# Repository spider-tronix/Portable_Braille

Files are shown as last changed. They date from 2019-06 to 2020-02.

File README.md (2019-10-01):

# Portable Braille

## Abstract:
Braille is a system of raised dots that allows visually impaired people to read tactilely. Currently, the number of books written in Braille script is less and the cost is high. This project is an approach to solve the problem of unavailability of many of the books and texts in Braille script. The Portable Braille consists of a camera module which captures the image of a printed text material and converts it into text format by using Optical Character Recognition(OCR). The characters in the text are converted into Braille characters(3x2 matrix form) and fed to the actuators. The actuators are the pins in the head of a dot matrix printer. The pins are actuated in such a way that it creates pressure at required points in the fingertip similar to how pressure felt when placed on an embossed braille character. By this way the device sends character by character to the user’s fingertip through the actuators.
These characters will be sent with appropriate delays to make the user understand words/sentences. Hence a given printed text material can be understood by the blind person through his/her sense of touch.

## Team:

  • [Aditya Kumar Singh](https://github.com/adityasingh3007)

  • [Raj Kumar Bhagat](https://github.com/Rajk0520)

  • [Ruphan S](https://github.com/ruphan)

  • [Yash Patel](https://github.com/yash270200)

## Working Video Demonstration:

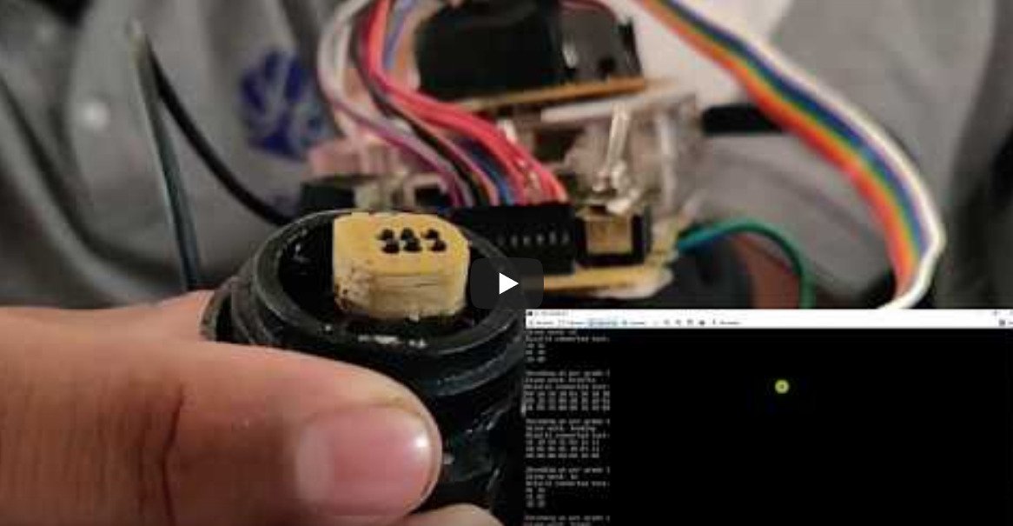
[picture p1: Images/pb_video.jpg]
(https://youtu.be/wZ1dMdXMtPE)

    
# Repository Organized.

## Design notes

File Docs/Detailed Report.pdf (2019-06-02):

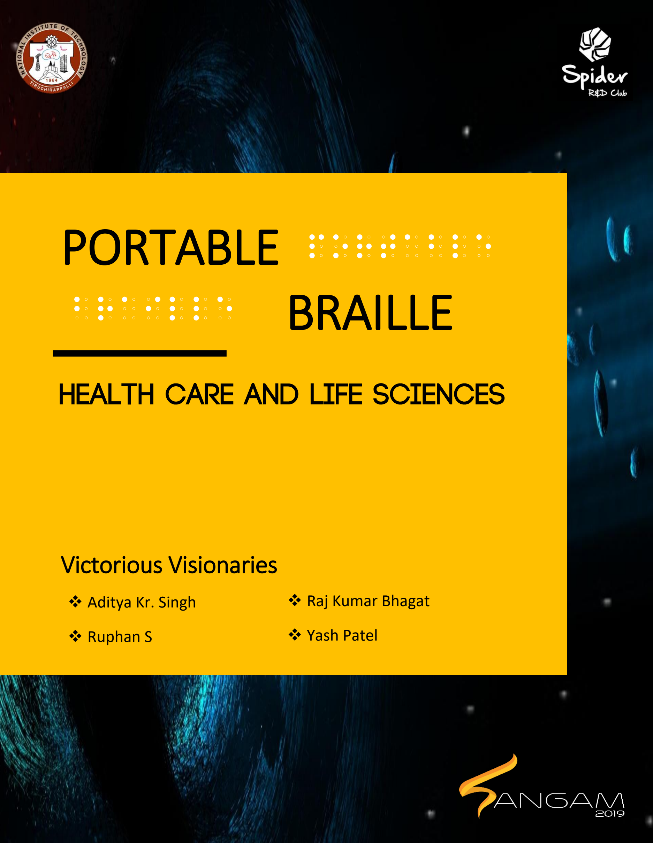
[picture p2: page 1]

1

# PORTABLE BRAILLE

## ❖ Aditya Kr. Singh

## ❖ Ruphan S

# Victorious Visionaries

# portable

# braille

## ❖ Raj Kumar Bhagat

## ❖ Yash Patel

## Portable Braille

2

# Table of Contents

### Project – Portable Braille System | 1

### Table of Contents | 2

1. | Introduction | | 3
2. | Proposed Solution (in Nutshell) | | 4
3. | Technical Details | | 5
3.1 Image Capturing | 5
3.2 OCR | 5
3.3 Braille Conversion | 6
3.4 Actuation | 7
4. | Extension | | 8
5. | Innovativeness | | 8
6. | Components and Cost | | 9
7. | Timeline | | 10
8. | Statistics and Impacts | | 11

3

B
raille is a system of raised dots that allows visually impaired people to read tactilely. Braille symbols are formed within units of space known as braille cells. A full braille cell consists of six raised dots arranged in two parallel rows each having three dots. The dot positions are identified by numbers from one through six. A single cell can be used to represent an alphabet letter, number, punctuation mark, or even a whole word depending upon the grade used. Braille is not just a language, rather it’s a code by means of which other languages such as English, Spanish, Arabic, and dozens of others may be read. Also, Braille defines the blind literacy. A blind person is considered to be a literate only if he/she knows to read Braille, hence making Braille a day-to-day need for the blind. This is also one of the main reason why Braille is still a standard and not completely obsolete.

Currently, the number of books written in Braille script are less and the cost is high. This project is an approach to solve the problem of unavailability of many of the books and texts in Braille script. The Portable Braille consists of a camera module which captures the image of a printed text material and converts it into text format by using Optical Character Recognition(OCR). The characters in the text are converted into Braille characters(3x2 matrix form) and fed to the actuators. The actuators are the pins in the head of a dot matrix printer. The pins are actuated in such a way that it creates pressure at required points in the fingertip similar to how pressure is felt when placed on an embossed braille character. The device sends character by character to the user’s fingertip through the actuators. These characters will be sent with appropriate delays to make the user understand words/sentences. Hence a given printed text material can be understood by the blind person through his/her sense of touch.

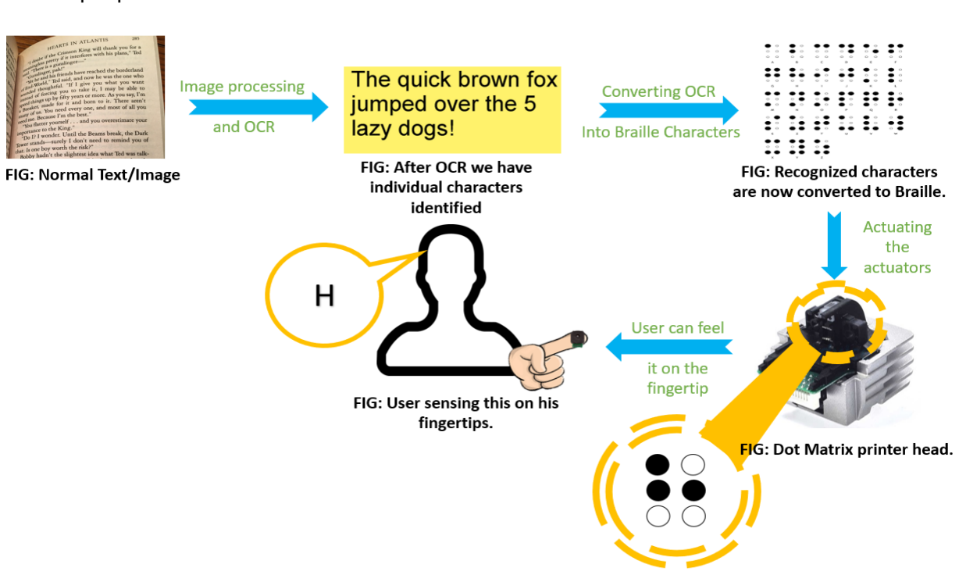
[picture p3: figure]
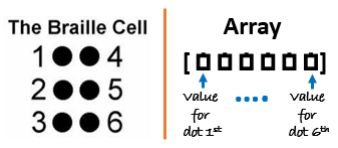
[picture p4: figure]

4

# (in Nutshell)

The proposed solution is as shown:

The user will wear a spectacle on which the camera module will be mounted. The camera will capture the view in front of it. The captured image will be processed and the portion having text in it will be considered for further processing and the rest will be discarded. Then the text image or the image under the consideration will be processed further using the OCR algorithm through ‘pytesseract’ library (this library takes the help from Google Tesseract application and recognizes the text on the image passed to it and return the text in string form) and the text present on the image will be recognized and stored in a string. Now, this string will be converted into its corresponding braille cell, character by character and stored in array form. The array is having six elements in it, representing 6 dots in a braille cell, with elements position mapped according to the braille cells position number. If the dot is meant to be raised the corresponding array element is 1 or
else 0. These arrays will be sent and
accordingly the actuators will be actuated
(for 1 the particular pin will be raised, for 0 no action or initial position).

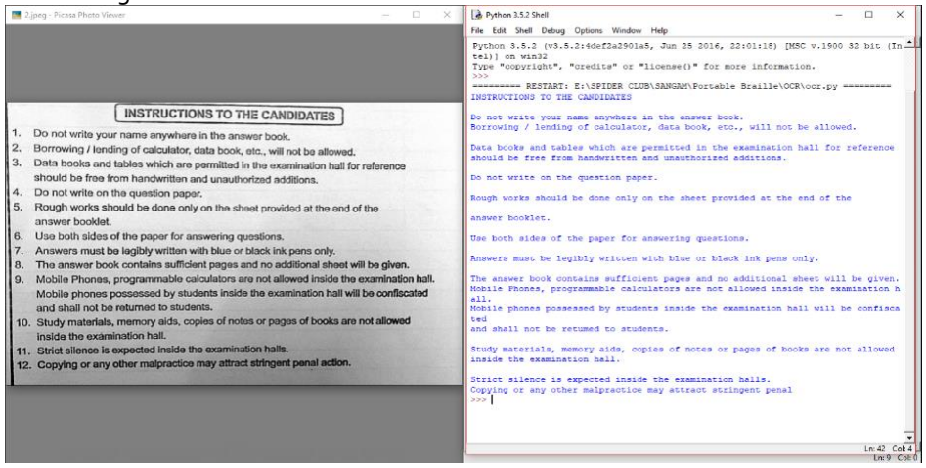
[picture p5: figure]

5

The whole process can be divided into 4 sections viz. Image Capturing, OCR, Braille Conversion, Actuation. Technicalities of the various section are described below:-

### Image Capturing:

Each user will be given a spectacle. On that a camera will be attached which will capture the image. Considering power utilization by the camera, the camera will not be continuously ON. Whenever the user wants to start reading, he/she will press a button and the camera will be turned ON. It will then capture 10-15 images and then turn OFF automatically. From these images a proper image will be chosen(the one with less blurriness and distortion). Hence the desired image is found from the captured photo burst. The best image is finally fed to the microcontroller. Then further image processing techniques like perspective transform and few threshold filters are applied to convert the captured image into a binary image of the required size. And finally, we use the OCR algorithm on this binary image to get the text in string format.

### Optical Character Recognition:

Google’s Tesseract-OCR (Optical Character Recognition) is used to identify individual characters in the image. ‘pytesseract’ is used as wrapping library for the Google’s Tesseract-OCR. Hence the given image can be converted from image format to text format as shown below.

FIGURE 1: Sample test image after OCR. (Lang: English)

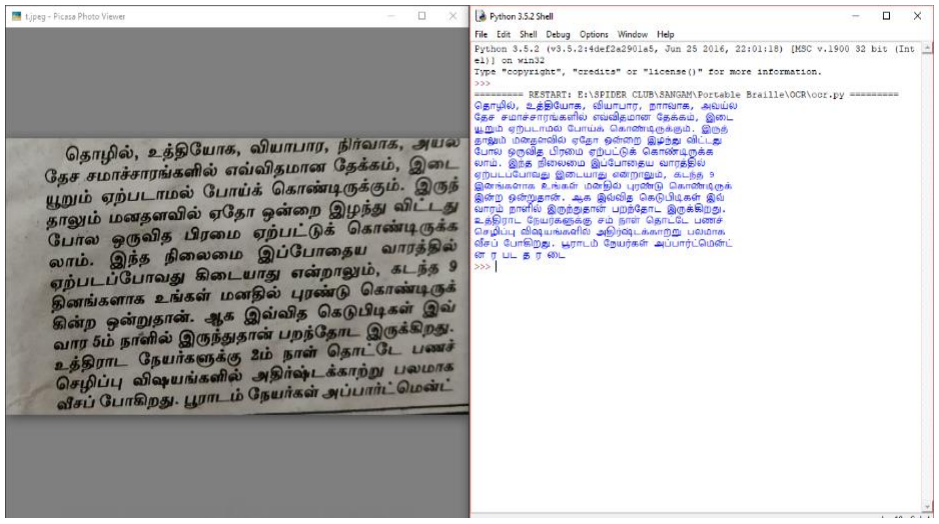
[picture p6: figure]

6

FIGURE 2: Sample test image after OCR. (Lang: Tamil)

The OCR will return the whole text in a string form. The string is stored and sent for braille conversion where each character will be converted into a 3x2 matrix.

### Braille Conversion:

The string obtained after applying OCR algorithm is translated into its corresponding braille cells character by character. Each character is converted into an array of 6 elements having 1 or 0 as its value, 1 if a dot is meant to be raised, 0 if not. The braille cell dots number is mapped according to the elements of the array. For example, H in braille form is represented as - h, now

the corresponding array form will be [1 1 0 0 1 0] since in the cell, dot 1,2,5(start numbering dots from top to bottom and starting from left) are raised and rest are not. So accordingly, 1

st,2nd,5th element in the array is 1 and rest all are 0. Like

this, all the characters are converted into its braille form and fed into the actuators. These actuators simulate braille by creating pressure in the fingertip at appropriate places. Also, the braille conversion can be done in two ways-using GRADE 1 or GRADE 2 Braille. Our code can convert according to both grades, the user has to choose it in its first run. If at all he/she wants to shift to another grade later he/she can do that. The difference in the Grades are as follows:

7

Grade 1 Braille: In this grade, each possible arrangement of dots within a cell represents only one letter, number, punctuation sign, or special Braille composition sign - it is a one-to-one conversion. Individual cells cannot represent words or abbreviations in this grade of Braille. Hence books were bulkier and larger than normally printed textbooks. This type of Braille is typically used only by those who are new to learning the grades of Braille.

Grade 2 Braille: This grade was introduced as a space-saving alternative to grade 1 Braille. In grade 2 Braille, a cell can represent a shortened form of a word. Many cell combinations have been created to represent common words, making this the most popular of the grades of Braille. There are part-word contractions, which often stand in for common suffixes or prefixes, and whole-word contractions, in which a single cell represents an entire commonly used word. Words may be abbreviated by using a single letter to represent the entire word, using a special symbol to precede either the first or last letter of the word while truncating the rest of the word, using a double-letter contraction such as "bb" or "cc", or removing most or all of the vowels in a word in order to shorten it. A complex system of styles, rules, and usage has been developed for this grade of Braille.

For example: - If you convert word “braille” into Braille cells, according to grade 1 the result will have 7 different cells representing each of the ‘b’, ‘r’, ‘a’……(all the letters), whereas, if you go with grade 2, the result will have only 3 cells for ‘b’, ‘r’, ‘l’ since “Braille” in grade 2 is abbreviated as “brl”. Hence, grade 2 saves space.

### Actuation:

The head of an old dot matrix printer is used as the actuator to simulate the Braille characters on the fingertip of a blind person. This is preferred compared to other alternatives such as Shape Memory Alloys(SMAs) and servos as the actuators in dot matrix printers are small enough to simulate a whole Braille character(3x2 matrix) in a single fingertip. An appropriate 3D printed structure can be used to change the arrangement of these actuators from linear fashion(9x1) into 3x2 matrix format.
After the Braille conversion step the array will be processed and where ever 1 is found, the signal will be pulled to HIGH in the printer head(terminal) for the corresponding pin to raise it. If 0 is found, signal will be pulled to LOW. Proper delay will be given to differentiate between words and sentences.

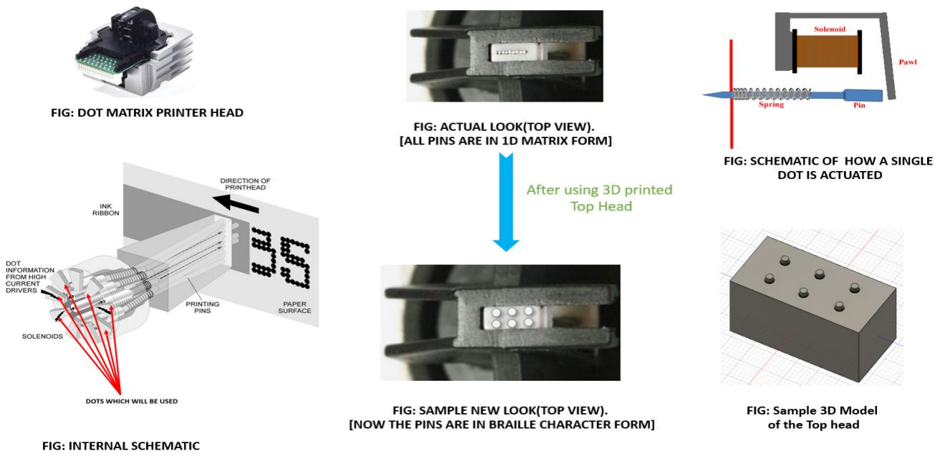
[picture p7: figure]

8

FIGURE 3

- Provision for controlling the speed at which braille characters are sent to the actuating units.
- Provision for storing text materials which can be read again later.
- Provision for choosing the language of the text to be read.
- Provision to have a memory so that user can roll back (10-15 characters) and once again start reading it.
- The existing prototype which has a similar objective can be found in the reference link. It uses Shape Memory Alloys as actuators in 3 fingers to simulate Braille characters.
- Our prototype is more practical as we are able to simulate the characters in a single fingertip.
- The actuation of Shape Memory Alloys is very slow compared to the actuation of the pins in the dot matrix printer head.
- Cost of our actuators is almost NIL(E-Waste) while Shape Memory Alloys are comparatively costlier.
- Reusing of e-waste (obsolete dot matrix printer head) for a useful cause.

9

COMPONENTS/PARTS | ROLE/FUNCTIONALITY
Raspberry Pi 3B | The main part of the project where all processing will take place.
Dot Matrix Printer Head | Used for miniaturized actuators
Pi Cam | Used for capturing the required image
Batteries | For powering the circuit
Few 3D printed parts | For fabrication
Other Electronic Components (Wires, Resistors, etc. ….) | For connection, limiting current, etc.

BUDGET:
The total estimated budget of the project is ₹ 6000/-

Budget breakdown is as follows:
Raspberry Pi 3B | ₹ 2749
Dot Matrix Printer Head | ₹ 0
Pi Cam | ₹ 1199
Battery (LiPo 11.3V) | ₹ 1599
3D Printing | ₹200
Other Electrical Components | ₹ 200
(Wires, Resistors, etc. ….)

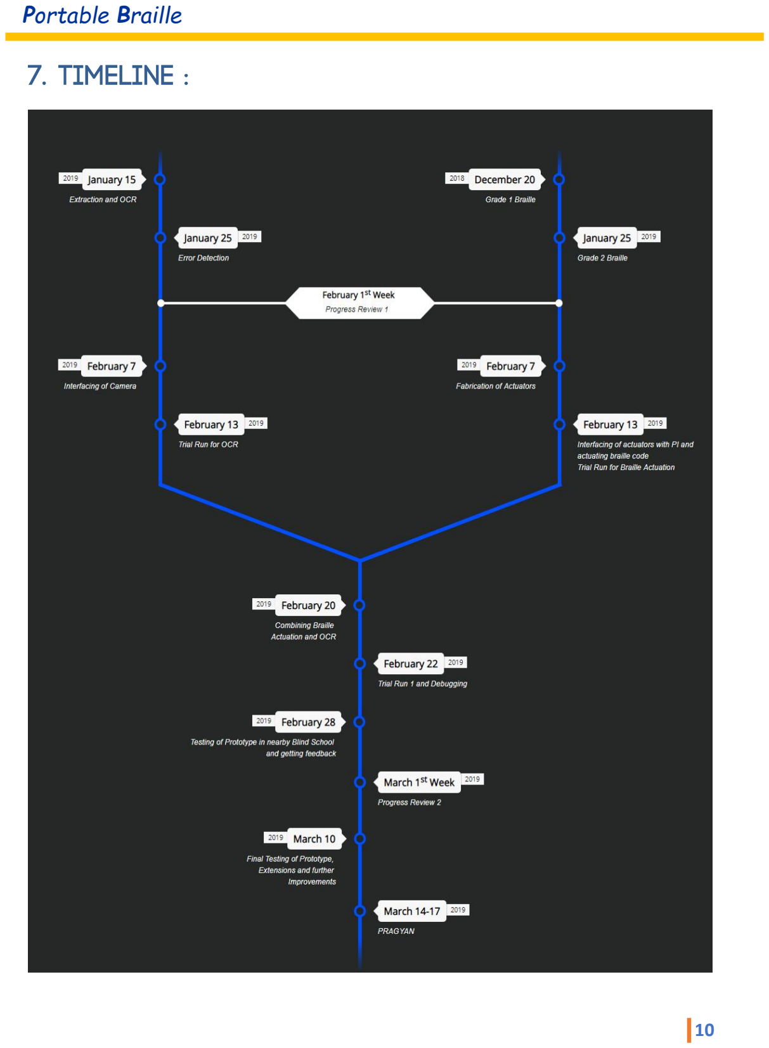
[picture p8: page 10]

10

11

- The National Federation of the Blind states that a blind person is considered to be a literate only if he/she knows Braille.
- According to the statistics of NCBI(National Centre for Biotechnology Information) of India, there are around 15000 blind schools in the country with about 200,000 blind students. All of them learn Braille and depend on it for their education. Hence this portable system has a direct impact on them as it gives access to all the texts a normal student could get.
- A major part of the blind population falls under the age category of senior citizens. These people use Braille for leisure activities unlike the children and young adults who use it for learning. This makes it more difficult for them to get the Braille form of texts they need, like daily newspapers.
- According to the Forbes article in the reference, the number of books available in Braille is well under 1% of the total literature. According to the website a Braille reader costs around 3000$-15000$(₹2,00,000 - ₹10,00,000Rs) which is too expensive compared to this portable reader which costs just ₹6000.

GitHub Repository link:
https://github.com/adityasingh3007/Portable_Braille

Google drive link:
https://drive.google.com/drive/folders/1wH5ih7TGFLmzVzSVHatiSTik0FH5W4lT

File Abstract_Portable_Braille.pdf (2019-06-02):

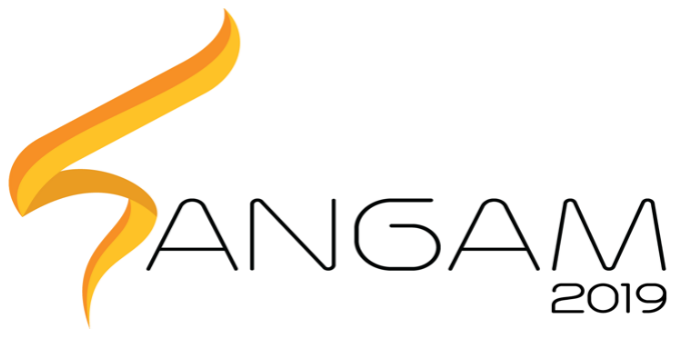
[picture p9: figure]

## PRAGYAN HARDWARE HACKATHON

## HEALTH CARE AND LIFE SCIENCES

## PORTABLE BRAILLE

## (Guided by Spider R&D Club)

Name | College ID/Roll UG/PG | Course/Branch Semester
Name | Roll Number | UG/PG | Branch | Semester
Aditya Kumar Singh | 107117004 | UG | EEE | 4
Raj Kumar Bhagat | 107117080 | UG | EEE | 4
Ruphan S | 107117086 | UG | EEE | 4
Yash Patel | 107117105 | UG | EEE | 4

### 1. Project Abstract:

Braille is a system of raised dots that allows visually impaired people to read tactilely. Currently, the number of books written in Braille script is less and the cost is high. This project is an approach to solve the problem of unavailability of many of the books and texts in Braille script. The Portable Braille consists of a camera module which captures the image of a printed text material and converts it into text format by using Optical Character Recognition(OCR). The characters in the text are converted into Braille characters(3x2 matrix form) and fed to the actuators. The actuators are the pins in the head of a dot matrix printer. The pins are actuated in such a way that it creates pressure at required points in the fingertip similar to how pressure felt when placed on an embossed braille character. By this way the device sends character by character to the user’s fingertip through the actuators.
These characters will be sent with appropriate delays to make the user understand words/sentences. Hence a given printed text material can be understood by the blind person through his/her sense of touch.
Keywords— Braille, Dot Matrix Printer Head, Solenoid, Linear Actuator, Optical Character Recognition(OCR), Portable, Reading Assistive Device.

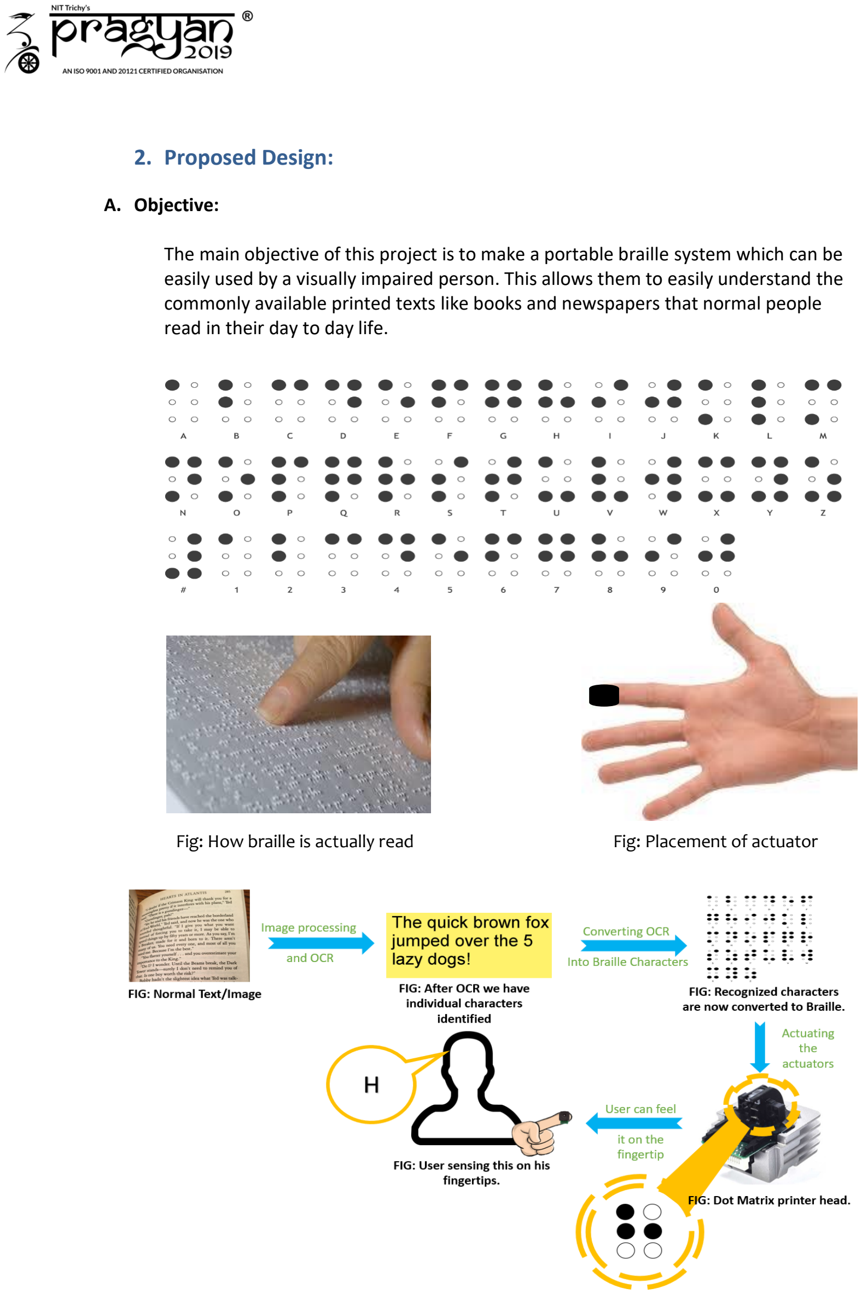
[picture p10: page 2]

### 2. Proposed Design:

A. Objective:

The main objective of this project is to make a portable braille system which can be easily used by a visually impaired person. This allows them to easily understand the commonly available printed texts like books and newspapers that normal people read in their day to day life.

Fig: How braille is actually read | Fig: Placement of actuator

B. Proposed Solution:
a. Block Diagram:

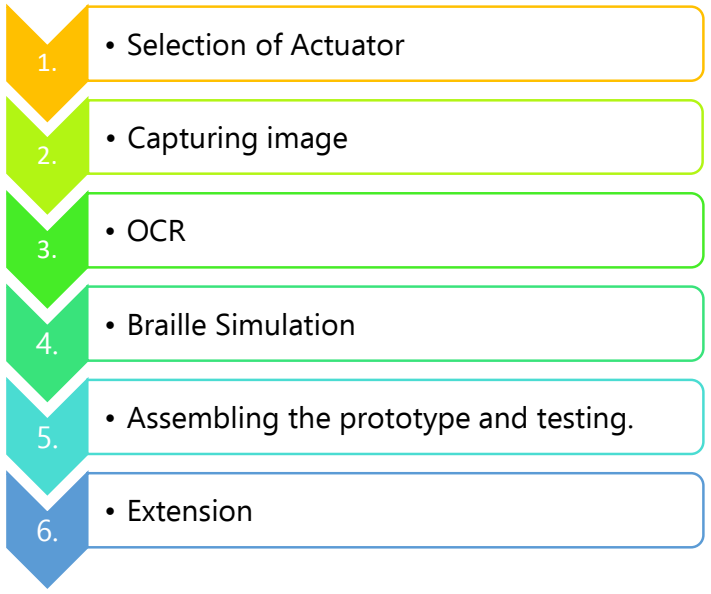
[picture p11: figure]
1. • Selection of Actuator; 2. • Capturing image; 3. • OCR; 4. • Braille Simulation; 6. • Extension

5. • Assembling the prototype and testing.

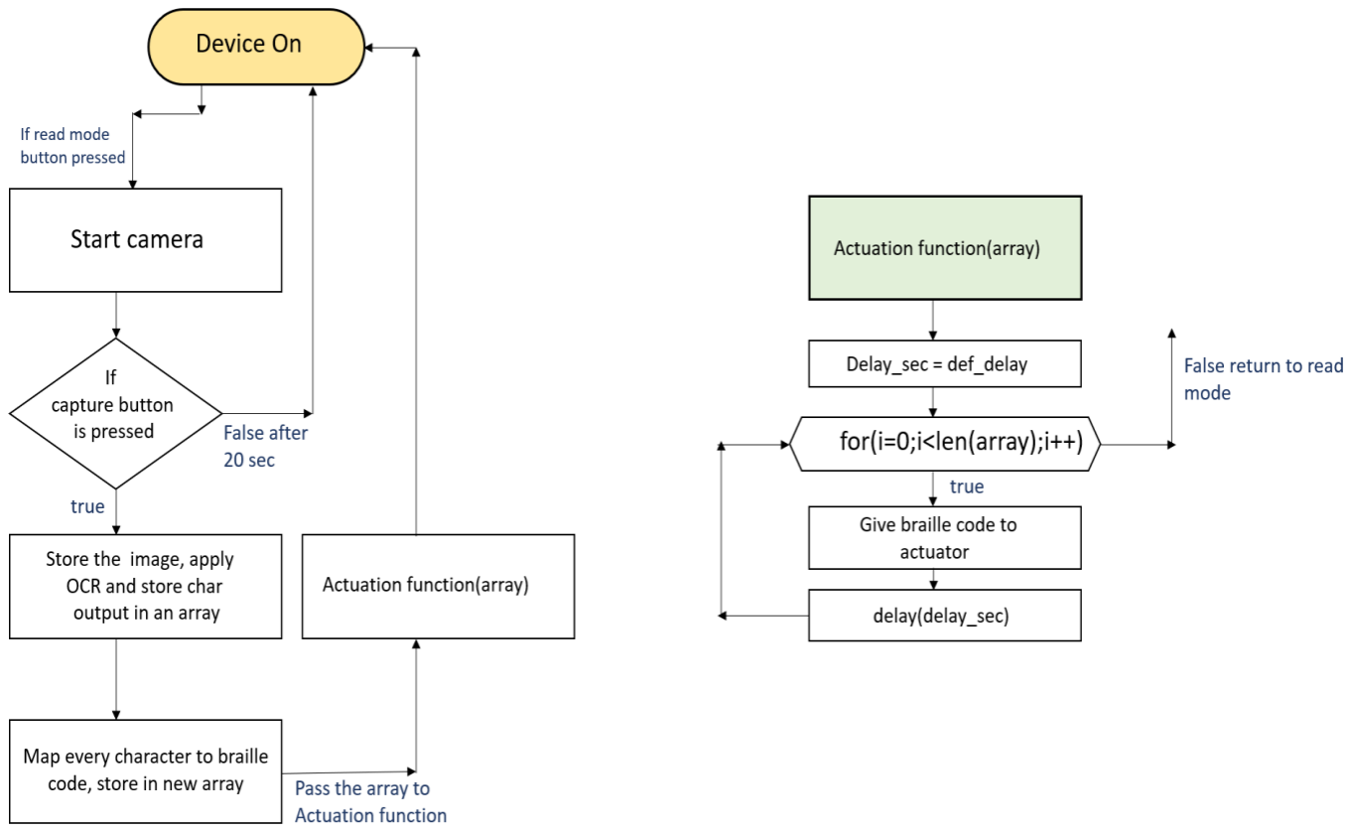
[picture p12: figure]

### 1. Selection of Actuator:

The head of an old dot matrix printer is used as the actuator to simulate the Braille characters on the fingertip of a blind person. This is preferred compared to other alternatives such as Shape Memory Alloys(SMAs) and servos as the actuators in dot matrix printers are small enough to simulate a whole Braille character(3x2 matrix) in a single fingertip. An appropriate 3D printed structure can be used to change the arrangement of these actuators from linear fashion(9x1) into 3x2 matrix format.

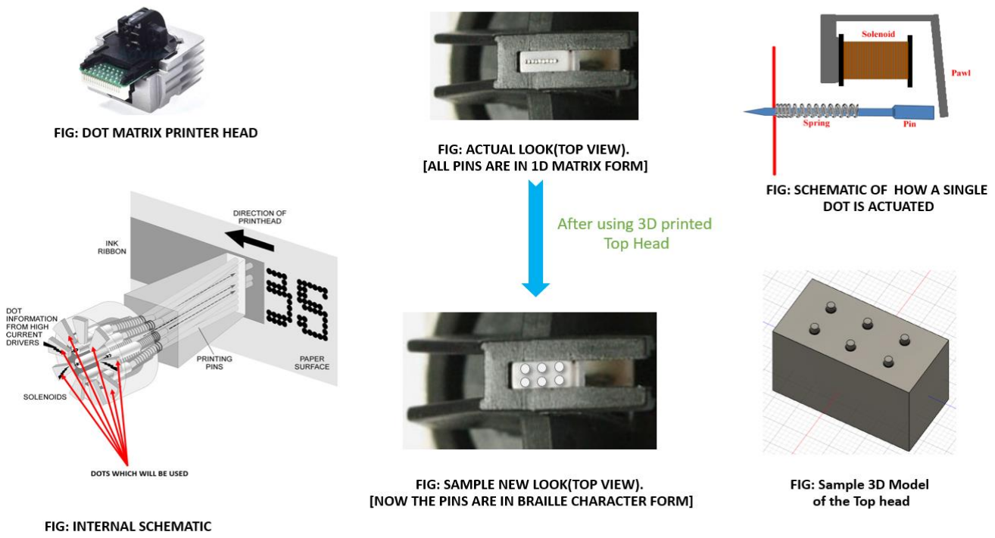
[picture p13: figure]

### 2. Capturing Image:

The image of a printed text material is captured through a camera and fed to the microcontroller. The required part is identified and cropped from the captured image. We add necessary filters before applying OCR.

### 3. OCR:

We use an appropriate algorithm for Optical Character Recognition (OCR) and identify individual characters in the image. Hence the given image can be converted from image format to text format.

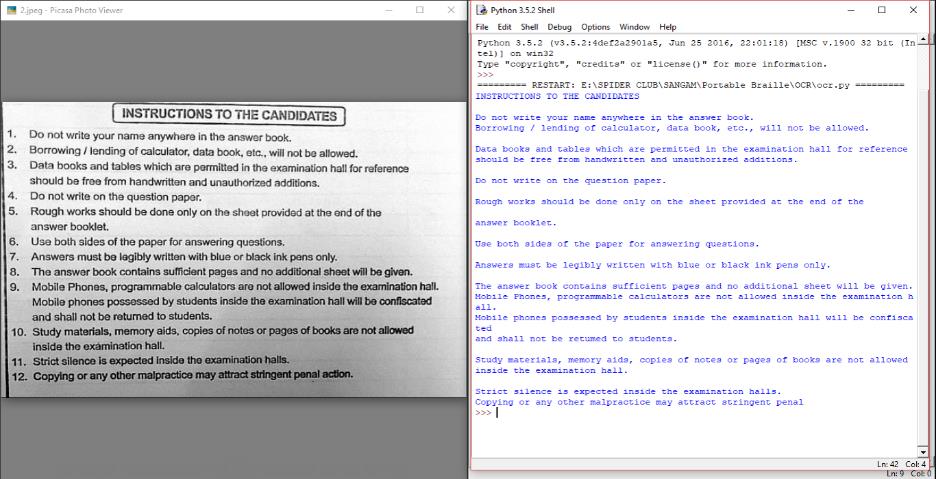
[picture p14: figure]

Snippet from answer booklet

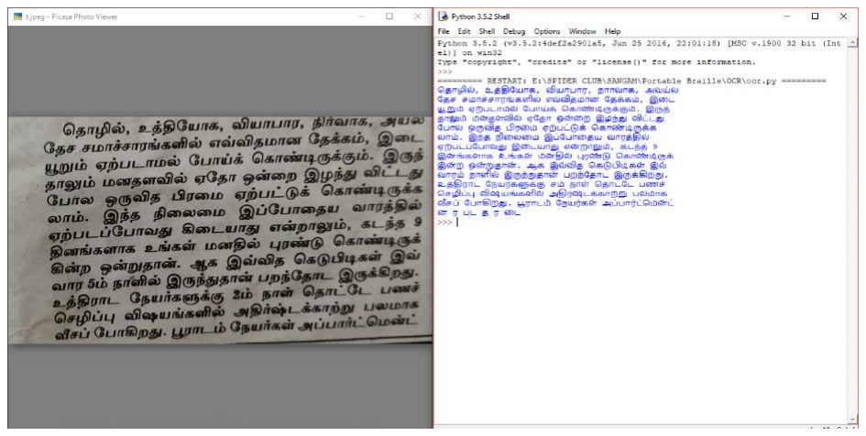
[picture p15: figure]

### 4. Braille Simulation:

The characters obtained after applying OCR algorithm is translated into its corresponding braille characters and fed into the actuators. These actuators simulate braille by creating pressure in the fingertip at appropriate places.

### 5. Assembling the prototype:

All the modules used in the prototype like microcontroller, camera, actuators and power circuits are placed in the required places with proper fabrication.

### 6. Extension:

- Provision for controlling the speed at which braille characters are sent to the actuating units.
- Provision for storing text materials which can be read again later.
- Provision for choosing the language of the text to be read.
C. Components Required:
COMPONENTS/PARTS | Role/functionality
Raspberry Pi | The main part of the project where all processing will take place.
Dot matrix Printer Head | Used for miniaturized actuators
Pi Cam | Used for capturing the required image
Batteries | For powering the circuit
Few 3D printed parts | For fabrication

### 3. Innovativeness of the Proposed Solution

- The existing prototype which has a similar objective can be found in the reference link. It uses Shape Memory Alloys as actuators in 3 fingers to simulate Braille characters.

Snippet from a Tamil newspaper

- This prototype is more practical as we are able to simulate the characters in a single fingertip.
- The actuation of Shape Memory Alloys is very slow compared to the actuation of the pins in the dot matrix printer head.
- Cost of our actuators is almost NIL(E-Waste) while Shape Memory Alloys are costly.
- Reusing of e-waste (obsolete dot matrix printer head) for a useful cause.

### 4. Impact of the proposed solution (Application):

- The National Federation of the Blind states that a blind person is considered to be a literate only if he/she knows Braille.
- According to the statistics of NCBI(National Centre for Biotechnology Information) of India, there are around 15000 blind schools in the country with about 200,000 blind students. All of them learn Braille and depend on it for their education.
- Hence this portable system affects them directly by giving them access to all the texts a normal student could get.
- A major part of the blind population falls under the age category of senior citizens. These people use Braille for leisure activities unlike the children and young adults who use it for learning. This makes it more difficult for them to get the Braille form of texts they need, like daily newspapers.
- According to the Forbes article in the reference, the number of books available in Braille is well under 1% of the total literature. According to the website a Braille reader costs around 3000$-15000$(~2,00,000Rs - ~10,00,000Rs) which is way too costlier than this portable reader.

### 5. References

1. https://ieeexplore.ieee.org/document/5167956
- A similar idea implemented with Shape Memory Alloys.
2. http://www.who.int/blindness/GLOBALDATAFINALforweb.pdf
- WHO report on global data for visually impaired people.
3. https://nfb.org/images/nfb/documents/pdf/braille_literacy_report_web.pdf
- Report of National Federation of Blind of America.
4. https://www.forbes.com/sites/timworstall/2012/08/18/this-digital-age-why-isnt-it-a-paradise-for-braille-readers/#6f43b3130e75 (https://www.forbes.com/sites/timworstall/2012/08/18/this-digital-age-why-isnt-it-a-paradise-for-braille-readers/)
- An article about why the digital world isn’t yet a paradise for the blind.

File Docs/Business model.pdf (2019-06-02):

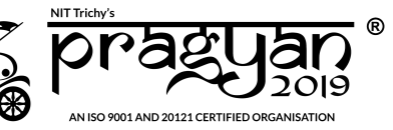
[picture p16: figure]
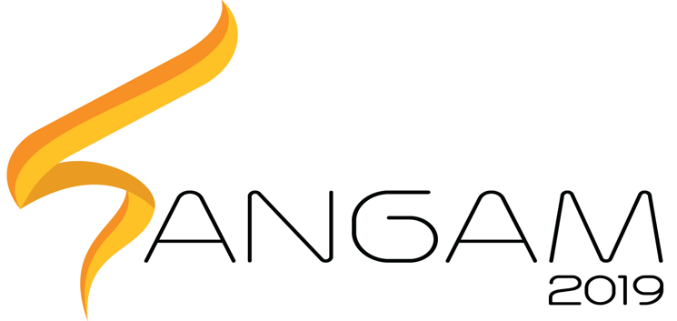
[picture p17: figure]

## PRAGYAN HARDWARE HACKATHON

## PORTABLE BRAILLE

Key resources:
The key components present in the product are Camera module, Micro processing unit and miniaturised actuators. Customised boards reduce the size and cost of the product drastically. Micro actuators are harvested from obsolete dot matrix printer heads which are of negligible cost. Collaborating with e-waste management organisations like Dell & Goodwill to get easy access to the printer head.

Value propositions :
- Similar Braille readers existing in market is at least 15-20 times costlier than this product ($2000 - $10,000). Those Braille readers are like e-braille books and can be used only if the content is preloaded unlike this product which captures images of any text and actuates them in Braille.
- Highly portable in nature, hence suitable for everyday usage.
- Large scale manufacturing of this product helps to reduce e-waste(obsolete dot matrix printer head)

Cost structure :
Micro processing unit (Rs.2000 – 3000), Camera module (Rs. 2000 – 3000) and Power source (LiPo battery – Rs. 1500)

Future work :
- This project has high scopes to become a marketable product as it has a big impact on the day to day lives of the blind people. Hence this product can be commercialized by associating with start-ups/companies like Forus health and GE Health care.
- Addition of other features like face/object recognition and feature to store ebooks can make this product a personalised assistant for visually impaired people.

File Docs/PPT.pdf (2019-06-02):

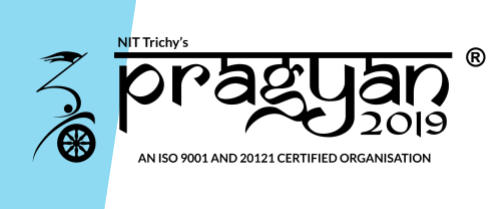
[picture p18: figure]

# Victorious Visionaries: Portable Braille

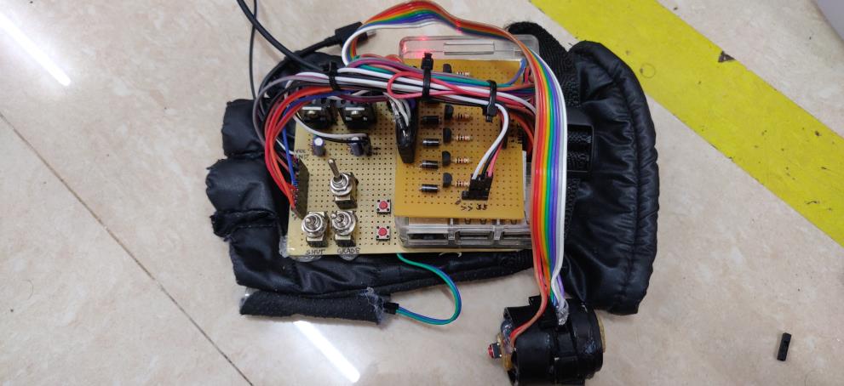
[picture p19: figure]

Aditya Kumar Singh
Raj Kumar Bhagat
Ruphan S
Yash Patel

# OBJECTIVE

## The aim of this project is to make a Portable Braille System as an assistive reading device to solve the problem of unavailability of many of the printed books

and texts in Braille script.

# WORK PLAN

- Implementation of text extraction from an image using Optical Character Recognition.(OCR)
- Implementation of text to Braille conversion in Grade 1 and Grade 2.
- Combining the above in Raspberry Pi to achieve image to braille code conversion.
- Modification of dot matrix printer head to act as an actuator.
- Adding extra features like speed variation and read mode, making driver circuit for actuation.
- Fabrication of the prototype and testing/feedback in blind home/school.

# STATUS

- Currently the model takes images and converts them to text format and then to Braille code and feeds this code to user’s fingertip by a dot-matrix printer head.
- A vibration motor is installed to give feedback to the user.
- Toggle switch is used to select between Grade 1 and Grade 2 Braille as per user convenience.
- Two push-buttons are given to adjust the speed at which the Braille code is actuated.

# FUTURE WORK

- Customized processing unit can be used to make a more compact model which also reduces the cost drastically.
- Using a memory unit to store the words, hence achieving a system of e-braille books.
- Rewind/Forward features can be added, so that the user can go forward or backward to some words if needed.
- Can be extended to handwritten and cursive text reading.
- Wireless interfacing between camera and processor to make the model more portable and user friendly.
- Object and face detection to make this system as a complete personal assistant for the blind.

Key Partners | Key Activities | Value Propositions | Customer
| • R&D to make this into a complete personal assistant or blind. | Relationship • Partnering with blind schools and rehabilitation centres.
| Key Resources • Miniaturized actuators obtained from obsolete printer heads. • Customized microprocessor. | Channels • Government organisations like NGOs, IAB, NAB.
Cost Structure • Processing unit : Rs.2000-3000. Can be reduced further with customized boards. • Camera: Rs. 2000-3000 | Revenue Streams • Rehabiliation centres for blind. • Governments organisations like governments schools for blind, IAB,NAB.

Customer
Segments

# BUSINESS MODEL PLAN

- GE Healthcare
- Forus Health
- IAB (Indian
Association for
Blind)
- NAB(National
Association for
Blind)
- Dell & Goodwill
e-waste
management
system
- Very cheap
compared to
existing braille
readers.
- Highly portable for
day to day usage.
- After few
extensions it can
become a
personalised
assistant for the
blind.
- Visually
impaired
students.
- People who
read regularly
in Braille.
- Blind
homes/Associ
ation.

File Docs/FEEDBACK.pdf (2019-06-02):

We tested the prototype in Rehabilitation centre for Blind Women in Trichy.

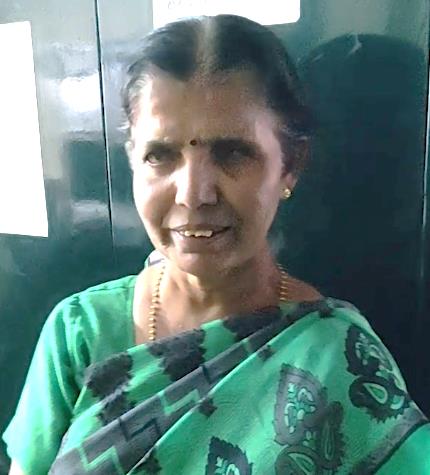
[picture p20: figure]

NAME : Regina Mary
AGE : 50+

Test 1: Since the product has only a single braille cell, the test subject found it difficult to identify the relative position of the embossed dots. She was also was not comfortable with the speed.

Test 2: Adjustable speed control was made and all the dots were embossed a little in normal state while the required dots were actuated above it. Hence the person felt it a lot more easier to recognise the characters.

Her feedback:

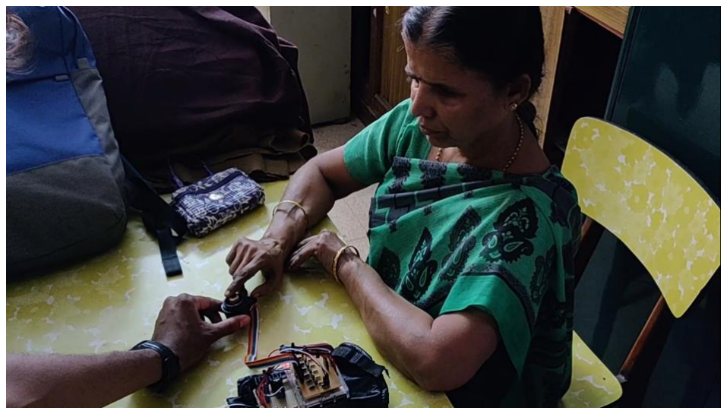
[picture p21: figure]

She was not able to read as fast as she reads in braille sheet as this was the first time, but reading felt a lot more comfortable and easier. She also said that with practice the reading speed can be improved a lot. She thanked us for creating such a product to help the blind community.

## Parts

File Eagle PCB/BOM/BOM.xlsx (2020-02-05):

Qty | Designator | Footprint | LCSC Part # | Description
3 | DRV8833PWP1, DRV8833PWP2, DRV8833PWP3 | SOP65P640X120-17N | C50506
8 | JP1, JP2, JP3, JP4, JP5, JP6, JP7, JP8 | 1X01 |  | PIN HEADER
3 | R1, R2, R3 | 0805 | C25336 | 0.22Ω resistor
3 | C3, C6, C9 | 0603 | C7248 | 0.01uF/10nF/10,000pF ceramic capacitors
3 | C1, C4, C10 | 0805 | C307523 | 10.0µF ceramic capacitors
3 | C2, C5, C8 | 0603 | C23630 | 2.2µF ceramic capacitors
1 | J7 | 61300211121 |  | CONN HEADER VERT 2POS 2.54MM
3 | J1, J4, J6 | 61300511121 |  | CONN HEADER VERT 5POS 2.54MM
2 | IC1, IC2 | SO16 | C431479 | 8-bit SHIFT REGISTER, output latch
1 | IC3 | SOT89 | C83866 | VOLTAGE REGULATOR

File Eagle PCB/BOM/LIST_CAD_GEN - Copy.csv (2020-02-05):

Qty | Value | Device | Package | Parts | Description
3 |  | DRV8833 | SOP65P640X120-17N | DRV8833PWP1, DRV8833PWP2, DRV8833PWP3
8 |  | PINHD-1X1 | 1X01 | JP1, JP2, JP3, JP4, JP5, JP6, JP7, JP8 | PIN HEADER
3 | 0.22 | 0.22OHM-0805-1/4W-1% | 805 | R1, R2, R3 | 0.220 Ω resistor
3 | 10nF | 10NF-0603-50V-10% | 603 | C3, C6, C9 | 0.01µF/10nF/10,000pF ceramic capacitors
3 | 10uF | 10UF-0805-10V-10% | 805 | C1, C4, C10 | 10.0µF ceramic capacitors
3 | 2.2uF | 2.2UF-0603-10V-20% | 603 | C2, C5, C8 | 2.2µF ceramic capacitors
1 | 61300211121 | 61300211121 | 61300211121 | J7 | CONN HEADER VERT 2POS 2.54MM
3 | 61300511121 | 61300511121 | 61300511121 | J1, J4, J6 | CONN HEADER VERT 5POS 2.54MM
2 | 74HC595D | 74HC595D | SO16 | IC1, IC2 | 8-bit SHIFT REGISTER, output latch
1 | L78LXXCU/BU | L78LXXCU/BU | SOT89 | IC3 | VOLTAGE REGULATOR

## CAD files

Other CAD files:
CAD Model/Basic CAD Model.dwg
CAD Model/Individual solenoid modules/S4.dwg
CAD Model/Individual solenoid modules/S3.dwg
CAD Model/Individual solenoid modules/S2.dwg
CAD Model/Individual solenoid modules/S6.dwg
CAD Model/Individual solenoid modules/S1.dwg
CAD Model/Individual solenoid modules/S5.dwg
CAD Model/Individual solenoid modules/Single Braille Cell.dwg
CAD Model/Individual solenoid modules/std_sol.dwg

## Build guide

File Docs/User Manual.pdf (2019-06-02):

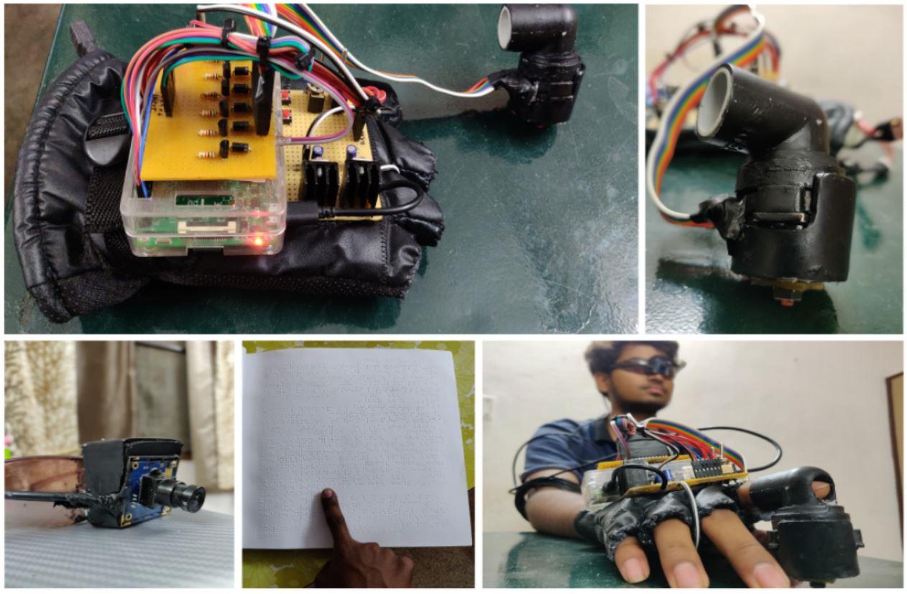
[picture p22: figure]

# Portable Braille

A READING ASSISTIVE DEVICE FOR VISUALLY IMPAIRED PERSON.

## (USER MANUAL)

## CONTENT

### 1. Getting Started | 2

### 2. Understanding Your Braille Device | 3

2.1 | Control Description | 3
2.2 | Working Description | 5

### 3. How To Use? | 6

### 4. Safety Information. | 8

## Getting Started

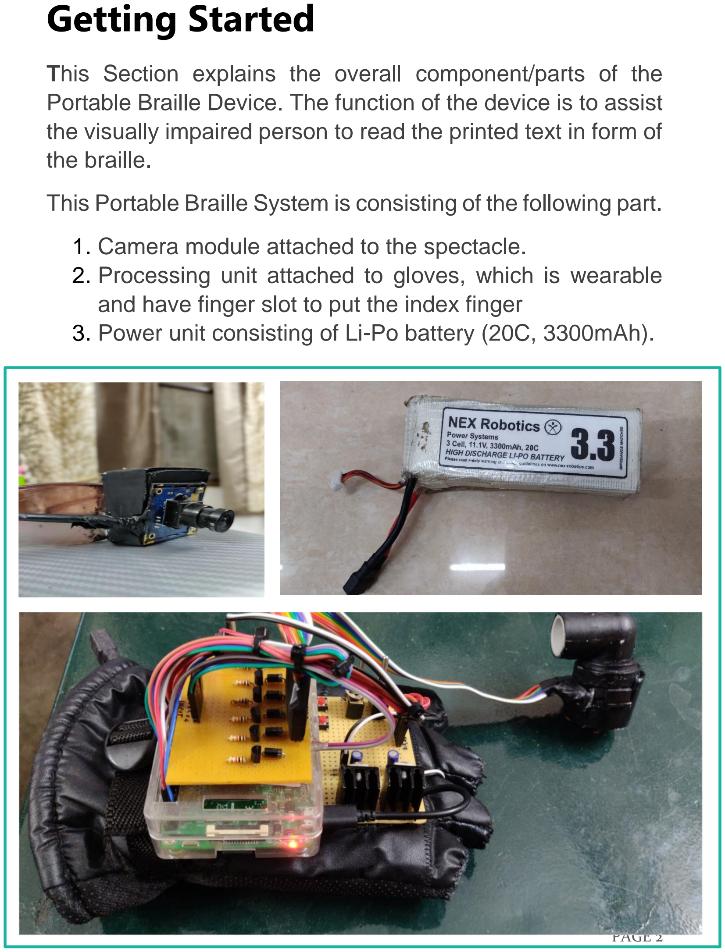
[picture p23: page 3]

This Section explains the overall component/parts of the Portable Braille Device. The function of the device is to assist the visually impaired person to read the printed text in form of the braille.

This Portable Braille System is consisting of the following part.

1. Camera module attached to the spectacle.
2. Processing unit attached to gloves, which is wearable and have finger slot to put the index finger
3. Power unit consisting of Li-Po battery (20C, 3300mAh).

## Understanding Your Device

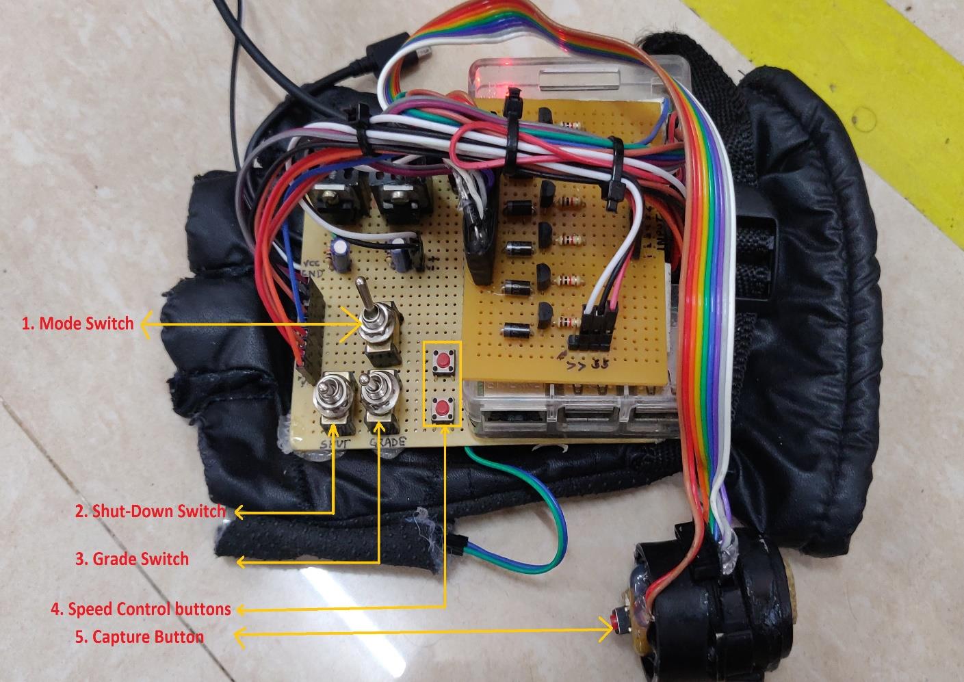
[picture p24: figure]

Control Description

There are five different Buttons/Switch to control the Device.

### 1. Mode Switch:

This switch is used to shift between A4 mode and book mode. For the right-handed person toggle the switch towards left for A4 mode and right for the book mode.

In A4 mode it will take image and directly process it to remove the unnecessary background.

In book mode it is difficult to directly process the image. So, in this mode user will have to give the coordinate information of the corner of the page by pressing the capture button at each corner position of the page.

### 2. Shut-Down switch:

This switch is to shut down the processor. Toggle this switch from its initial position to shut down the processors.

### 3. Grade Switch:

This switch is to shift between the Grade 1 and Grade 2 braille. For the right-handed person toggle the switch towards left for Grade 1 and right for Grade 2.

### 4. Speed control buttons:

These two buttons are used to adjust the reading speed as per the user convenience. For the right-handed person left-side button will decrease the reading speed by 0.1 seconds and the right-side button will increase the speed by 0.1 seconds.

### 5. Capture Button:

This button is attached to the bottom of braille terminal. In A4 mode this button is used to capture the image. In Book mode it is used to capture the coordinate of each corner of a page and then taking the required image.

Working Description

This device works in the following four steps.

### 1. Image Capturing:

The camera module which is attached to the spectacle will capture the image of the printed text.

A4 mode:
To capture the image user will have to press the push button attached to the braille terminal.

If the printed text is not in the frame of the camera it will give vibration feedback for 2 seconds stating image taken is not proper to be processed further. At this point user has to adjust the printed text position with respect to the camera and take the new image till there is no vibration feedback.

Book mode:
In this mode user will have to give the coordinate information of the corner of the page by pressing the capture button at each corner position of the page. The image will be automatically captured after all the four corner is detected.

### 2. OCR (Optical Character Recognition):

After getting the proper image the device will apply OCR in the image and extract the text from it.

### 3. Braille Conversion:

As per the choice of grade (either grade 1 or grade 2, chosen with the help of toggle Grade switch) by the user, the extracted text will be converted to corresponding braille grade.

### 4. Actuation:

After the braille conversion the actuation will start in the braille terminal. The user can then adjust the speed as per his/her convenience.

## How to use?

Step 1:

Wear the glove, tighten it properly. Choose the Grade (1 or 2) and Mode (A4 or book). Keep the index finger inside the braille terminal.

Step 2:

Wear the spectacle and switch on the device. If user feels three vibration then the battery is sufficiently charged. If not, then the battery is low and it should be charged before next use.

Step 3:

Now keep the printed text material near the camera such that the full text material should come inside the camera view.

In A4 mode:

Press the terminal button to capture the image. If the printed text is not in the frame of the camera it will give vibration feedback for 2 seconds stating image taken is not proper to be processed further. At this point user has to adjust the printed text position with respect to the camera and take the new image till there is no vibration feedback.

In book mode:

Press the capture button at each corner of the page.

Step 4:

The actuation is started in the braille terminal. Adjust the speed as per the convenience using the speed control button.

Step 5:

After the reading is completed, toggle the shutdown switch to shut down the processor. After this switch off the power switch to completely turnoff the device.

## Safety Information

1. Do not overcharge the battery.
2. If there is any heating in the device, turn-off the device immediately.
3. Do not power off the device without shutting down the processor (use shut down toggle switch).
4. Do not use the device with wet hand.

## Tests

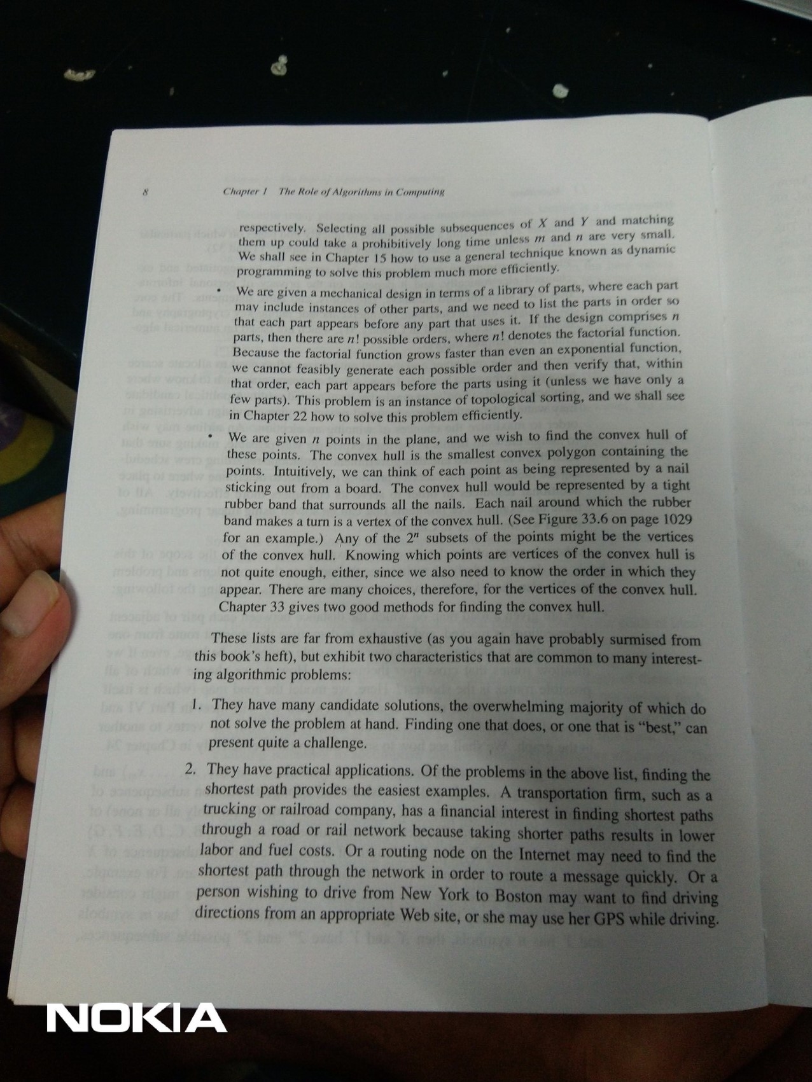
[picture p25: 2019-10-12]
Images/test1_0.jpg

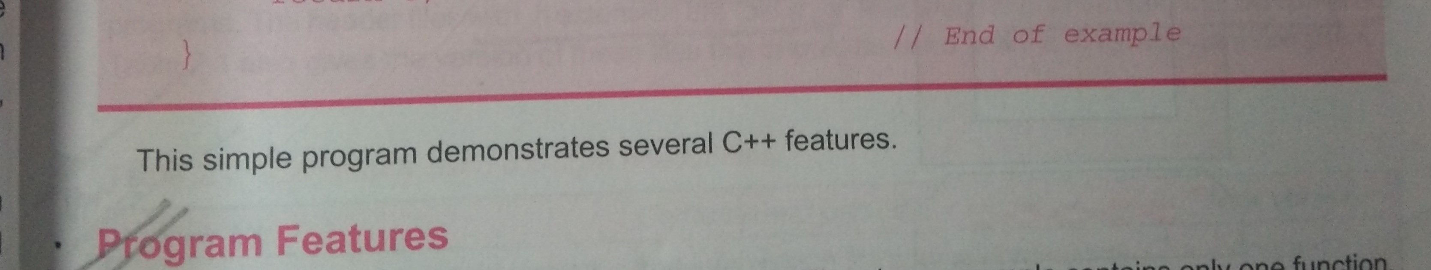
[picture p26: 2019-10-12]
Images/tesseract test/cropped.jpg

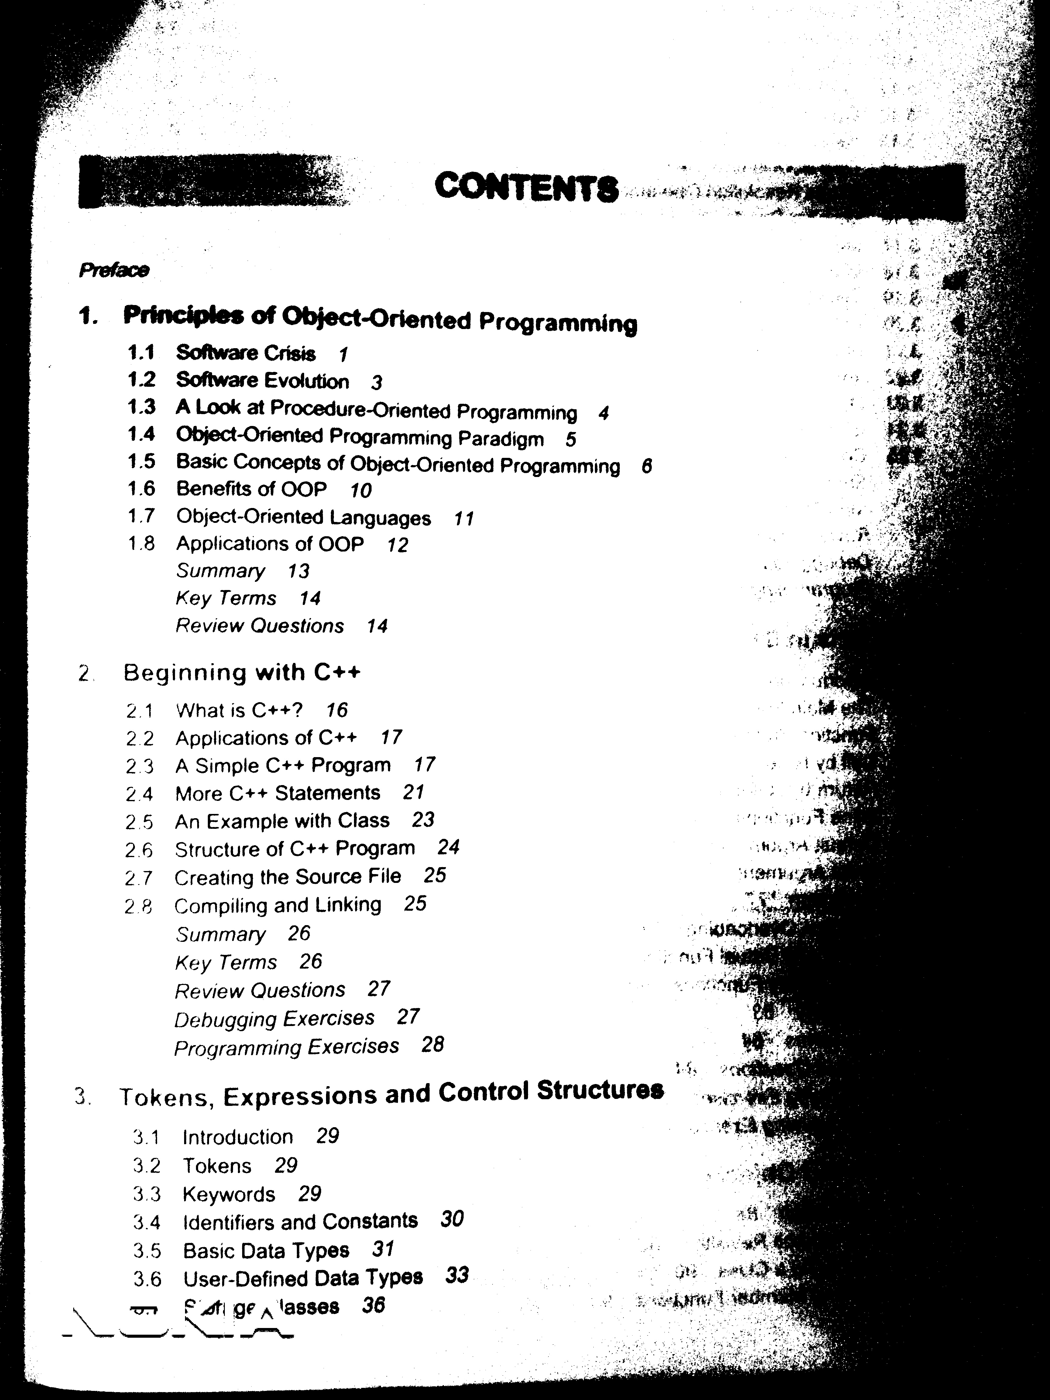
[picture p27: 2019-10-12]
Images/tesseract test/threash2.jpg

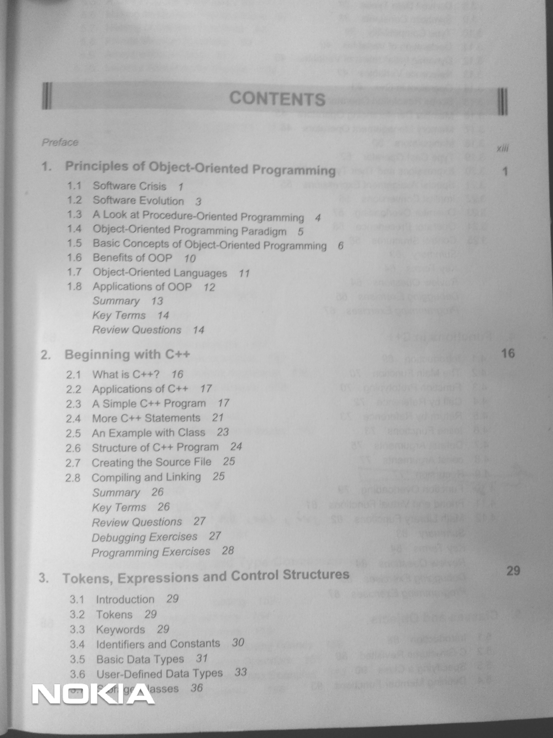
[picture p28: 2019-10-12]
Images/tesseract test/bw.jpg

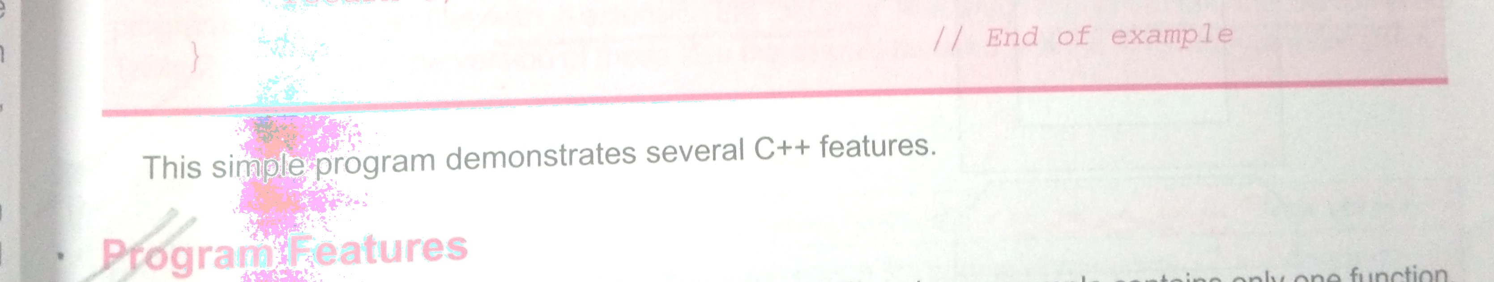
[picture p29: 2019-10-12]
Images/tesseract test/brighten.jpg

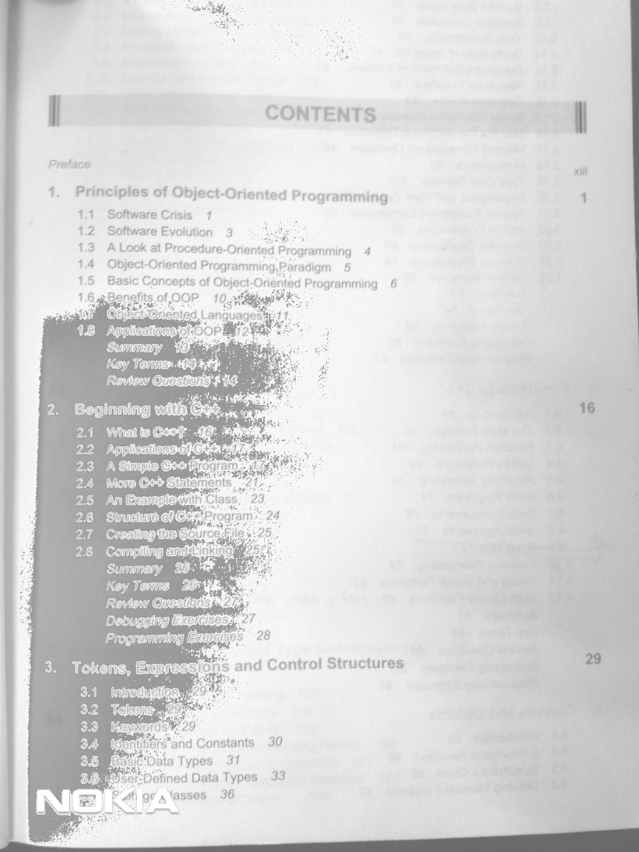
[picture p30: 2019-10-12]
Images/tesseract test/bw2.jpg

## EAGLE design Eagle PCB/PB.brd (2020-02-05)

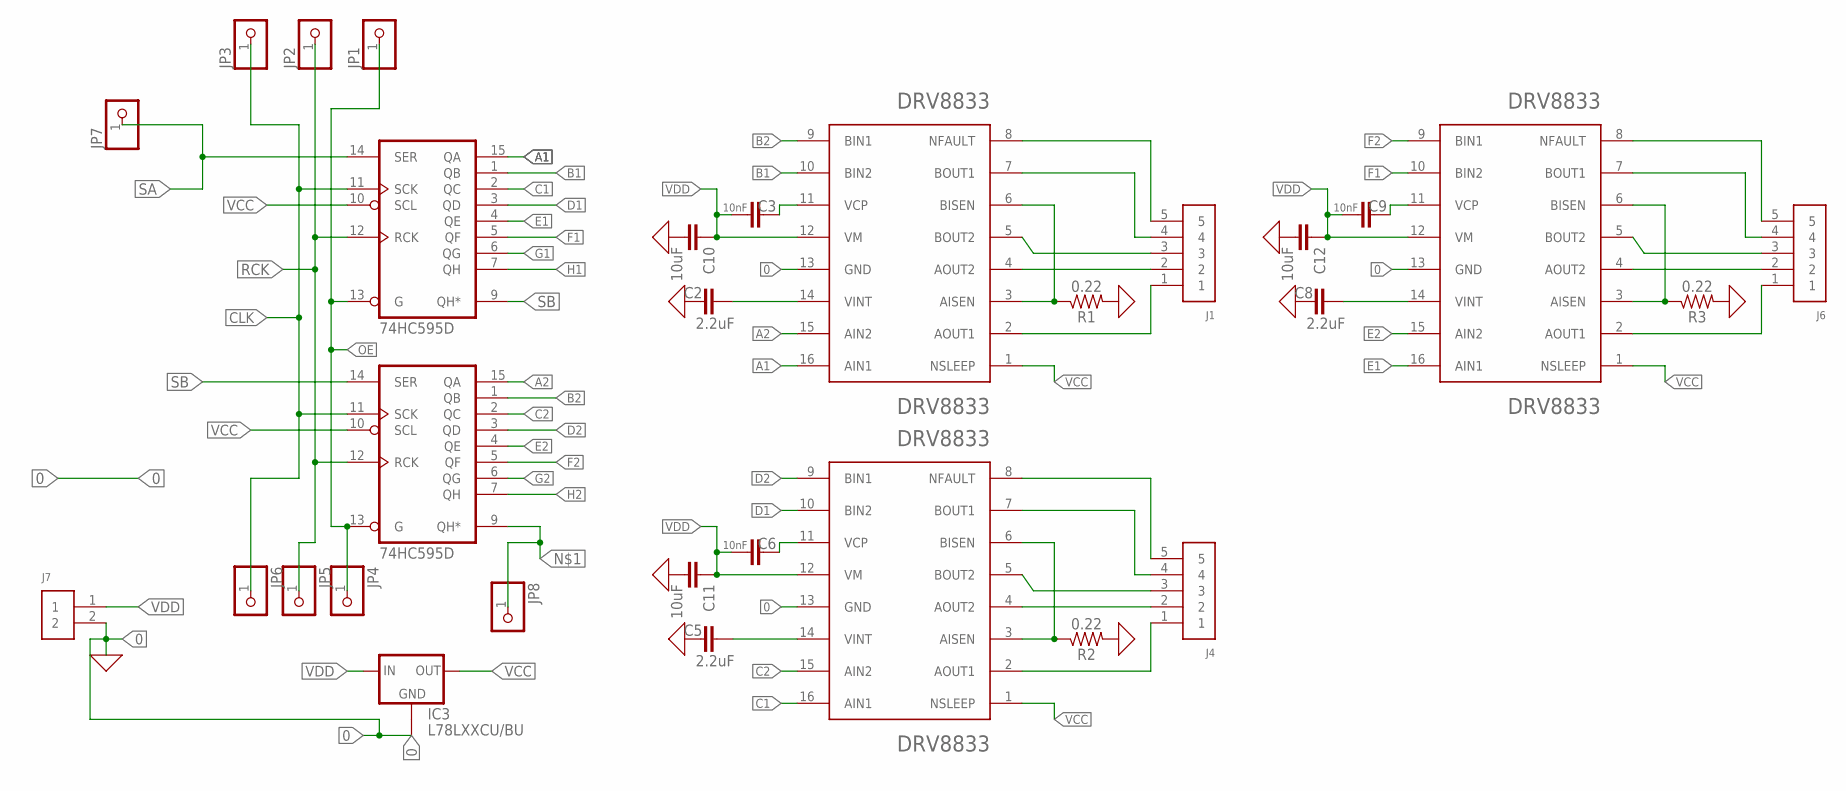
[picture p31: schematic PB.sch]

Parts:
C2, C5, C8: 2.2uF; 0603
C3, C6, C9: 10nF; 0603
C10, C11, C12: 10uF; 0805
DRV8833PWP1, DRV8833PWP2, DRV8833PWP3: DRV8833; SOP65P640X120-17N
IC1, IC2: 74HC595D; SO16
IC3: L78LXXCU/BU; SOT89
J1, J4, J6: 61300511121
J7: 61300211121
JP1, JP2, JP3, JP4, JP5, JP6, JP7, JP8: PINHD-1X1; 1X01
R1, R2, R3: 0.22; 0805

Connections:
0: C2.2, C5.2, C8.2, C10.2, C11.2, C12.2, DRV8833PWP1.13 (GND), DRV8833PWP2.13 (GND), DRV8833PWP3.13 (GND), IC1.8 (GND), IC2.8 (GND), IC3.4 (GND1), J7.2, R1.2, R2.2, R3.2
A1: DRV8833PWP1.16 (AIN1), IC1.15 (QA)
A2: DRV8833PWP1.15 (AIN2), IC2.15 (QA)
B1: DRV8833PWP1.10 (BIN2), IC1.1 (QB)
B2: DRV8833PWP1.9 (BIN1), IC2.1 (QB)
C1: DRV8833PWP2.16 (AIN1), IC1.2 (QC)
C2: DRV8833PWP2.15 (AIN2), IC2.2 (QC)
CLK: IC1.11 (SCK), IC2.11 (SCK), JP3.1, JP6.1
D1: DRV8833PWP2.10 (BIN2), IC1.3 (QD)
D2: DRV8833PWP2.9 (BIN1), IC2.3 (QD)
E1: DRV8833PWP3.16 (AIN1), IC1.4 (QE)
E2: DRV8833PWP3.15 (AIN2), IC2.4 (QE)
F1: DRV8833PWP3.10 (BIN2), IC1.5 (QF)
F2: DRV8833PWP3.9 (BIN1), IC2.5 (QF)
G1: IC1.6 (QG)
G2: IC2.6 (QG)
H1: IC1.7 (QH)
H2: IC2.7 (QH)
unnamed: IC2.9 (QH*), JP8.1
unnamed: C2.1, DRV8833PWP1.14 (VINT)
unnamed: C3.1, DRV8833PWP1.11 (VCP)
unnamed: DRV8833PWP1.3 (AISEN), DRV8833PWP1.6 (BISEN), R1.1
unnamed: DRV8833PWP1.8 (NFAULT), J1.5
unnamed: DRV8833PWP1.7 (BOUT1), J1.4
unnamed: DRV8833PWP1.2 (AOUT1), J1.1
unnamed: DRV8833PWP1.4 (AOUT2), J1.2
unnamed: DRV8833PWP1.5 (BOUT2), J1.3
unnamed: C5.1, DRV8833PWP2.14 (VINT)
unnamed: C6.1, DRV8833PWP2.11 (VCP)
unnamed: DRV8833PWP2.3 (AISEN), DRV8833PWP2.6 (BISEN), R2.1
unnamed: DRV8833PWP2.8 (NFAULT), J4.5
unnamed: DRV8833PWP2.7 (BOUT1), J4.4
unnamed: DRV8833PWP2.2 (AOUT1), J4.1
unnamed: DRV8833PWP2.4 (AOUT2), J4.2
unnamed: DRV8833PWP2.5 (BOUT2), J4.3
unnamed: C8.1, DRV8833PWP3.14 (VINT)
unnamed: C9.1, DRV8833PWP3.11 (VCP)
unnamed: DRV8833PWP3.3 (AISEN), DRV8833PWP3.6 (BISEN), R3.1
unnamed: DRV8833PWP3.8 (NFAULT), J6.5
unnamed: DRV8833PWP3.7 (BOUT1), J6.4
unnamed: DRV8833PWP3.2 (AOUT1), J6.1
unnamed: DRV8833PWP3.4 (AOUT2), J6.2
unnamed: DRV8833PWP3.5 (BOUT2), J6.3
OE: IC1.13 (G), IC2.13 (G), JP1.1, JP4.1
RCK: IC1.12 (RCK), IC2.12 (RCK), JP2.1, JP5.1
SA: IC1.14 (SER), JP7.1
SB: IC1.9 (QH*), IC2.14 (SER)
VCC: DRV8833PWP1.1 (NSLEEP), DRV8833PWP2.1 (NSLEEP), DRV8833PWP3.1 (NSLEEP), IC1.10 (SCL), IC1.16 (VCC), IC2.10 (SCL), IC2.16 (VCC), IC3.1 (OUT)
VDD: C3.2, C6.2, C9.2, C10.1, C11.1, C12.1, DRV8833PWP1.12 (VM), DRV8833PWP2.12 (VM), DRV8833PWP3.12 (VM), IC3.3 (IN), J7.1

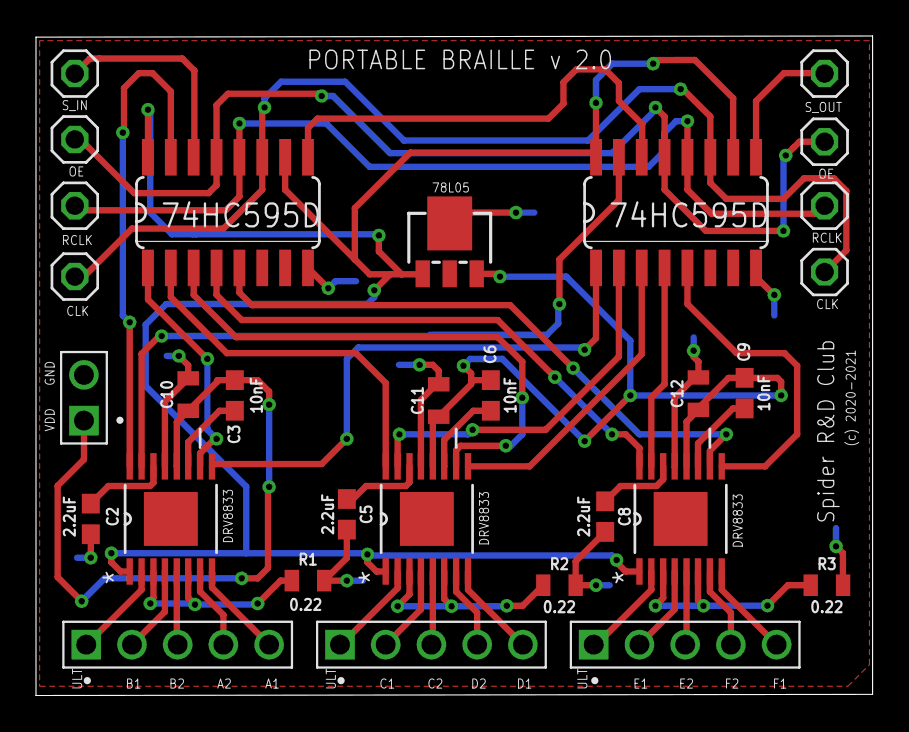
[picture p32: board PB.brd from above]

Board: 2 copper layers, 46.5 x 36.6 mm, 30 parts (0 on the bottom side), 45 nets.

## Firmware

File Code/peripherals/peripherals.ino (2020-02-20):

const int trigPin = 9;
const int echoPin = 10;

long duration;
int distance;
void setup() {
  pinMode(trigPin, OUTPUT); 
  pinMode(echoPin, INPUT); 
  Serial.begin(9600); 
}
void loop() {
  digitalWrite(trigPin, LOW);
  delayMicroseconds(2);
  digitalWrite(trigPin, HIGH);
  delayMicroseconds(10);
  digitalWrite(trigPin, LOW);
  duration = pulseIn(echoPin, HIGH);
  distance = duration * 0.034 / 2 -5;
  Serial.print("Distance: ");
  Serial.println(distance);
}

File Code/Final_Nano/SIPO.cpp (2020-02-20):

#include "SIPO.h"

#define RCLK 5
#define SER 4
#define SRCLK 6
#define EN 3

void setEnable_PWM(int val){
  analogWrite(EN,val);
}

SipoClass::SipoClass(){
    pinMode(SER, OUTPUT);
    pinMode(RCLK, OUTPUT);
    pinMode(SRCLK, OUTPUT);
    pinMode(EN, OUTPUT);
    ClearBuffer();
    setEnable_PWM(255);
}

void SipoClass::ClearBuffer()
{
  for (int i = TotalICPins - 1; i >=  0; i--)
  {
    Data[i] = LOW;
  }
  UpdateReg();
}

void SipoClass::UpdateReg(){
    digitalWrite(RCLK, LOW);
    for (int i = TotalICPins - 1; i >=  0; i--)
    {
        digitalWrite(SRCLK, LOW);
        digitalWrite(SER, Data[i]);
        digitalWrite(SRCLK, HIGH);
    }
    digitalWrite(RCLK, HIGH);
}

void SipoClass::print_data(){
  Serial.print("\nSIPO array Content: ");
  for(int i=0;i<80;i++){
    Serial.print(Data[i]);
    Serial.print(" ");
    if((i+1)%8==0)
      Serial.print("\n");
  }
  Serial.print("\n");
}
void SipoClass::set_data(unsigned char cell[], int pos[]){
  int start_index=1;
  int last_index=1;
  if(pos[0]==1){
    start_index=2;
  }
  else if(pos[1]==1){
    start_index=3;
  }
  else if(pos[2]==1){
    start_index=4;
  }
  else if(pos[3]==1){
    start_index=5;
  }
  else if(pos[4]==1){
    start_index=6;
  }
  else if(pos[5]==1){
    start_index=7;
  }
  last_index=start_index+3;
  //Overwriting 0 before starting cells
  for(int i=0;i<(start_index-1)*8;i++){
    Data[i]=0;
  }
  //Putting the reuired content
  for(int i=(start_index-1)*8;i<(last_index)*8;i++){
    Data[i]=cell[i]-48;
  }
  //Overwriting 0 after the last cell
  for(int i=(last_index)*8;i<80;i++){
    Data[i]=0;
  }
}

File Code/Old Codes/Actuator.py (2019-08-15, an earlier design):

# -*- coding: utf-8 -*-
"""
**************************************************************************************
*                              Actuator
*                           =============
*  This software is intended to convert english text into braille characters
*  MODULE: Actuator
*  Filename: Actuator.py
*  Version: 1.0.0  
*  Date: February 9, 2019
*  
*  Author: Aditya Kumar Singh
*  Team Name: Victorious Visionaries
*  Team Members: Aditya Kumar Singh, Raj Kumar Bhagat,
*                Ruphan S, Yash Patel
***************************************************************************************
"""

#Importing required libraries
from time import sleep
import RPi.GPIO as GPIO

"""
    Function which initialises all the required PINs in OUTPUT mode.
    And give logic 0 output to thr pins initially.
    Example call: init()
"""
def init():
    GPIO.setwarnings(False)
    GPIO.setmode(GPIO.BOARD)
    GPIO.setup(11, GPIO.OUT)
    GPIO.setup(12, GPIO.OUT)
    GPIO.setup(13, GPIO.OUT)
    GPIO.setup(15, GPIO.OUT)
    GPIO.setup(16, GPIO.OUT)
    GPIO.setup(18, GPIO.OUT)
    set_all_low()

"""
    Function which sets all the PINs to digitaly LOW state.
    Example call: set_all_low()
"""    
def set_all_low():
    GPIO.output(11, GPIO.LOW)
    GPIO.output(12, GPIO.LOW)
    GPIO.output(13, GPIO.LOW)
    GPIO.output(15, GPIO.LOW)
    GPIO.output(16, GPIO.LOW)
    GPIO.output(18, GPIO.LOW)

"""
    Function which maps the given array index to its corresponding PIN number
    to which it is attached to RPi adn returns the PIN number on RPi.
    Example call: x = get_pin_number(5)
"""
def get_pin_number(pin):
    str_= -1
    # Pins which are to be used from Rpi for actuatng.
    # 12 11 13 15 16 18
    if(pin==0):
        str_=16
    elif(pin==1):
        str_=18
    elif(pin==2):
        str_=12
    elif(pin==3):
        str_=15
    elif(pin==4):
        str_=11
    elif(pin==5):
        str_=13
    return str_

"""
    Function to set the particular PIN as HIGH or LOW depending upon the argument
    passed.
    Example Call: set_port_pin(0,0) to make pin 0 LOW,
                  set_port_pin(0,1) to make pin 0 HIGH 
"""
def set_port_pin(pin,value):
    ret=get_pin_number(pin)
    if(value):
        #HIGH
        GPIO.output(ret, GPIO.HIGH)
    else:
        GPIO.output(ret, GPIO.LOW)
        #LOW

"""
    Function to set the braille terminal according the Braille value passed.
    Example Call: actuate([1,1,1,0,0,0])
"""
def actuate(brl):
    index=0
    for i in brl:
        set_port_pin(index,i)
        index+=1
"""
    Function to clean GPIO PINs used in the module.
    Example Call: clean()
"""
def clean():
    GPIO.cleanup()
    
init()

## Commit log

2019-09-11 Basic solenoid schematic to reduce power consumption
2019-12-22 Camera Calibration Matrix
2019-12-22 Basic 3D Design of the setup
    [Basic_PB.dwg]
2019-12-23 Added extentsion mechanism for placing the book
    [Basic_PB.dwg]
2019-12-23 Added Camera Setup
    [Basic CAD Model.dwg, Basic_PB.dwg]
2019-12-23 Added Camera Mechanism
    [Basic CAD Model.dwg]
2020-01-19 Revert "Added Camera Mechanism"
    This reverts commit 3f9a1a776d8217dc012b96e9d371ecbb299fbd20.
    [Basic CAD Model.dwg]
2020-01-19 Added solenoid CAD models
    [std_sol.dwg]
2020-01-19 Added Single Braille Cell
    [S1.dwg, S2.dwg, S3.dwg, S4.dwg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]
2020-01-20 PCB schematic and board added
    [PB.brd, PB.sch]
2020-01-21 Added complete actuator setup
    [Single Braille Cell.dwg]
2020-01-26 client socket for table detection
2020-01-27 Final PCB schematic and board added.
    [PB.brd, PB.sch]
2020-02-05 PCB updated with common serial input.
    [PB.brd, PB.sch]
2020-02-05 Gerber files and BOM file added
    [BOM.xlsx, LIST_CAD_GEN - Copy.csv, LIST_CAD_GEN.csv, top.csv]

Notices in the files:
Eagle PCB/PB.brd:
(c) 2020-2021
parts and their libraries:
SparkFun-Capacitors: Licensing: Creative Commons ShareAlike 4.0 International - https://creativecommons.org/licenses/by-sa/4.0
